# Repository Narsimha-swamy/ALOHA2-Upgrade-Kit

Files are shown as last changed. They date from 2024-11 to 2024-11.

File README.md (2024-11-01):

# Overview 
This is repository is dedicated to upgrading Trossen Robotics ALOHA v1 to ALOHA v2. Bimanual manipulation is an important part of robotics for development of humanoid robots. An enhanced Low cost Open-source HArdware (ALOHA) offers hardware capable of performing bimanual manipulation tasks with a precision of 5-8mm with the ability to collect data via real-time teleoperation. Because of its affordable price many labs  all over the world have bought it from Trossen robotics. But soon after that the team developing ALOHA has released ALOHA v2 to mitigate couple problems that now ALOHA v1 had. The upgrades include new cameras, changed frame, gravity compensation supports for the teleoperator side leader robots and redesigned grippers for low-friction to reduce latency. In this repository you can find different ways you can upgrade the ALOHA v1, the material bill for each of the parts and a zip file that  includes . 

# Details 
The upgrade for ALOHA v2 can be done in 3 stages and these stages are independent of each other and can be done in any order based on the requirement and budget. All the items required for the upgrade are mentioned in the ALOHA 2 upgrade kit excel file the prices are dated as of 10/31/2024. All the cad models required for 3d printing are present in the aloha2 cad models directory.

Stage I - Camera upgrades : This upgrade can be done simply by 3d printing the camera mounts found in the cad models directory and replacing the existing logitech c922x Pro webcams to the new Realsense d405 depth cameras. Optionally if the PC connected to ALOHA doesn't have enough USB ports a 4 port USB Interface PCIe card can installed to the cpu since the cameras need to be connected directly to the motherboard and not the usb hub. This upgrade offers the ability to collect depth, point cloud and voxels data with some processing. 

Stage II - Gripper upgrades : This is the most expensive upgrade in ALOHA 2. This step requires precise 3d prints of both the follower and leader gripper, for its need to be low friction. To build the grippers follow the steps mentioned in the Google's ALOHA 2 Build Instrucitons google doc. And the gripper motors are replaced with the new dynamixel XC430-W150 motors.This upgrade offers better latency during teleoperation. 

Stage III - frame upgrade : This is the most time taking upgrade. This can be done in two approaches 1. Money efficient, 2. Time efficient.  For Money efficient approach we reuse the frame from ALOHA 1, by cutting the frame in required dimensions, by choosing this method you can save $205(USD). In depth tutorial for this will be uploaded soon. For the time efficient upgrade the extrusion bars mentioned in the ALOHA2 upgrade kit can be bought and install it using the procedure mentioned in the Google's ALOHA2 Build Instructions doc. This upgrade offers better frame stability and much better gravity compensation compared to ALOHA v1.

# Notice
All the cad models and the work related to the upgrade belong to the Google'2 ALOHA 2 team. The work in this repository only include a condensed and neat approach to upgrade ALOHA v1 to ALOHA v2 considering both cost and time efficient approaches,  and provide all resources required for the upgrade in one place.

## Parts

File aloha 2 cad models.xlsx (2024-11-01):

Name | Quantity
Mounts
Gravity compensator clip, wrist mount | 2 | Print settings
Gravity compensator clip, elbow mount | 2 | Nylon (pa6)
Camera mount for Viper wrist cam | 2 | Layer height 0.2
Overhead cam mount | 2 | 35-ish% infill, triangular
Worms-eye cam mount | 1 | 4 floor/ceiling layers, 2 wall layers
Widow x gripper
W-bridge_rails_support_v1 1 | 2
W-finger_adaptor_v1 | 4
W-finger_holder_M_v1 | 2
W-gripper_backplate_v1 (acrylic 3mm thickness) | 2
W-hand_holder_v1 | 2
W-rotor_arm_v1 | 4
W-rotor_v1 | 2
W-shim_rotor_v1 | 2
Viper x GRipper
Bridge_rails_support_v1 | 2
Finger_adaptor_v1 | 4
Finger_v1 | 2
Gripper_backplate_v1(acrylic 3mm thickness) | 2
Rotor_arm_v1 | 4
Rotor_v1 | 2
Shim_rotor_v1 | 2
Total 3d prints | 18

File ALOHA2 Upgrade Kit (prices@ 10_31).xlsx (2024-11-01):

Items | Distributor | Qty per package | Qty for one cell | Required packages | Link | Package Price | Price
Frame and Gravity Compensation
8PCS/Set Surface Anodic Oxidation Black L Shape Corner Bracket Plate 5-Hole Outside Joining Plate for 2020 Series Aluminum Profile 3D Printer Frame (Black L-8) | Amazon | 8 | 12 | 2 | https://www.amazon.com/dp/B07ZLSPRXP/ref=twister_B07SZDZG4K?_encoding=UTF8&th=1 | $15.99 | $31.98
316 Stainless Steel Button Head Hex Drive Screws, M5 x 0.8mm Thread, 8mm Long | McMaster | 50 | 70 | 2 | https://www.mcmaster.com/94500A230/ | $8.72 | $17.44
M5 x 12 button head screw, qty 50 | McMaster | 50 | 16 | 1 | https://www.mcmaster.com/92095A210/ | $10.01 | $10.01 | Frame and gravity compensation
M5 x 8 button head screw, qty 100 | McMaster | 100 | 64 | 1 | https://www.mcmaster.com/92095A207/ | $16.33 | $16.33 | $506.16
M5 Post-Assembly Insertion Spring Nuts for 5 Series Aluminum Extrusions | Misumi | 100 | 120 | 2 | https://us.misumi-ec.com/vona2/detail/110302247640/?ProductCode=PACK-SHNTP5-5 | $57.07 | $114.14
Flat-Surface Bracket, 1-7/8" Square | McMaster | 1 | 7 | 7 | https://www.mcmaster.com/1030A15/ | $1.55 | $10.85
Automatic-Return Hanging Retractor without Cable Lock, 1 to 2 lb. Capacity | McMaster | 1 | 2 | 2 | https://www.mcmaster.com/6495A61/ | $55.48 | $110.96
Pulley for Wire Rope-for Horizontal Pull, Single-Groove with Bearing, Swivel Eye, for 3/16" Diameter Rope | McMaster | 1 | 6 | 6 | https://www.mcmaster.com/3213T57/ | $17.24 | $103.44
Music Wire Steel Extension Spring with Loop Ends, 5" Long, 0.5" OD, 0.037" Wire Diameter | McMaster | 3 | 2 | 1 | https://www.mcmaster.com/5108N531/ | $11.52 | $11.52
Rope Guide for 5/8" Maximum Rope Diameter, 316 Stainless Steel | McMaster | 1 | 6 | 6 | https://www.mcmaster.com/8860T129/ | $5.66 | $33.96
8 Pack: 4mm Black Cotton Macramé Cord by Bead Landing | Michaels | 1200 | 3 | 1 | https://www.michaels.com/product/8-pack-darice-craft-designer-cotton-macrame-cord-MP392109 | $45.53 | $45.53
Cameras and Wires
Realsense d405 | Digikey | 1 | 4 | 4 | https://www.digikey.com/en/products/detail/intel-realsense/82635DSD405MP/16265565?s=N4IgTCBcDaIE4FMCGAbAzggdhgBAEwBYAGAVhAF0BfIA | $278.75 | $1115.00 | Camera and wires
USB 3.0 Interface Card PCIe, Fresco FL1100, 4HC, x4, 4Ports | Basler | 1 | 1 | 1 | https://www.baslerweb.com/en-us/shop/usb-3-0-interface-card-pcie-fresco-fl1100-4hc-x4-4ports/ | $195.00 | $195.00 | $1510.49
Female Molex to Male SATA power adapter | Amazon | 3 | 1 | 1 | https://www.amazon.com/Power-Cable-Adapter-Female-8-inch/dp/B07BQFKTG7?s=industrial | $8.99 | $8.99
Sabrent 4-Port USB Hub, USB 3.0 Fast Data Hub with Individual LED Power Switches, 2 Ft Cable, Slim & Portable, for Mac & PC (HB-UM43) | Amazon | 1 | 1 | 1 | https://www.amazon.com/Sabrent-4-Port-Individual-Switches-HB-UM43/dp/B00JX1ZS5O?cv_ct_cx=usb+hub&sbo=RZvfv%2F%2FHxDF%2BO5021pAnSA%3D%3D | $14.50 | $14.50
USB 3.0 A Male to Micro B Male Up Angle with optional Screw Locking Cable, 3m | NTC | 1 | 1 | 1 | https://www.ntcdistributing.com/usb-3-0/a-to-micro-b/a-to-angled-b-cables/usb-3-0-a-male-to-micro-b-male-up-angle-with-optional-screw-locking-cable/ | $42.00 | $42.00
USB 3.0 A Male to Micro B Male Up Angle with optional Screw Locking Cable, 5m | NTC | 1 | 1 | 1 | https://www.ntcdistributing.com/usb-3-0/a-to-micro-b/a-to-angled-b-cables/usb-3-0-a-male-to-micro-b-male-up-angle-with-optional-screw-locking-cable/ | $47.00 | $47.00
USB 3.0 A Male to Micro B Male with M2 Screw Locking Cable, 3m | NTC | 1 | 1 | 1 | https://www.ntcdistributing.com/usb-3-0/a-to-micro-b/a-to-micro-b-with-screw-locking/usb-3-0-a-male-to-micro-b-male-with-m2-screw-locking-cable/ | $40.00 | $40.00
USB 3.0 A Male to Micro B Male with M2 Screw Locking Cable, 5m | NTC | 1 | 1 | 1 | https://www.ntcdistributing.com/usb-3-0/a-to-micro-b/a-to-micro-b-with-screw-locking/usb-3-0-a-male-to-micro-b-male-with-m2-screw-locking-cable/ | $48.00 | $48.00
Grippers
6725K27_5 mm Wide x 120 mm Long Rail Ball Bearing Carriage | McMaster | 1 | 4 | 4 | 6725K23 (https://www.mcmaster.com/6725K23-6725K27/) | $57.60 | $230.40
6725K27_5 mm Wide x 150 mm Long Rail Ball Bearing Carriage | McMaster | 1 | 4 | 4 | 6725K23 (https://www.mcmaster.com/6725K23-6725K28/) | $72.00 | $288.00 | Grippers upgrade
8438K1_Corrosion-Resistant Ball Bearing Carriage | McMaster | 1 | 16 | 16 | 8438K1 (https://www.mcmaster.com/8438K1/) | $92.04 | $1472.64 | $2365.03
Deep Groove Ball Bearing (3mmx6mmx2.5mm) | Amazon | 20 | 24 | 2 | Amazon (https://www.amazon.com/gp/product/B075CMRGY6/ref=ppx_yo_dt_b_asin_image_o01_s00?ie=UTF8&psc=1) | $13.99 | $27.98
M2 Brass Male-Female / Female-Female | Amazon | 1 | 1 | 1 | Amazon (https://www.amazon.com/gp/product/B07ZSZW8T1/ref=ppx_yo_dt_b_asin_title_o05_s00?ie=UTF8&psc=1) | $12.99 | $12.99
Flat Head Screw M3 x 0.5 mm Thread, 10 mm Long | McMaster | 100 | 16 | 1 | 92125A130 (https://www.mcmaster.com/92125A130/) | $7.31 | $7.31
Flat Head Screw M3 x 0.5 mm Thread, 20 mm Long | McMaster | 100 | 8 | 1 | 92125A136 (https://www.mcmaster.com/92125A136/) | $12.86 | $12.86
Flat Head Screw M2 x 0.4 mm Thread, 10 mm Long | McMaster | 100 | 88 | 1 | 92010A005 (https://www.mcmaster.com/92010A005/) | $5.84 | $5.84
Flat Head Screw M2 x 0.4 mm Thread, 16 mm Long | McMaster | 100 | 16 | 1 | 92010A0 08 (https://www.mcmaster.com/92010A008/) | $6.23 | $6.23
Flat Head Screw M2 x 0.4 mm Thread, 20 mm Long | McMaster | 100 | 24 | 1 | 92095A106 (https://www.mcmaster.com/92095A106/) | $5.62 | $5.62
Socket Head Screw M2 x 0.4 mm Thread, 6 mm Long | McMaster | 100 | 8 | 1 | 91292A831 (https://www.mcmaster.com/91292A831/) | $9.28 | $9.28
Hex Nut M2 x 0.4 mm Thread | McMaster | 100 | 64 | 1 | 91828A111 (https://www.mcmaster.com/91828A111/) | $6.14 | $6.14
Flat Head Screw M2.5 x 0.45 mm Thread, 16 mm Long | McMaster | 100 | 16 | 1 | 93395A185 (https://www.mcmaster.com/93395A185/) | $5.62 | $5.62
Steel Washer for M2 Screw Size, 2.200 mm ID, 4.500 mm OD | McMaster | 100 | 32 | 1 | 98688A110 (https://www.mcmaster.com/98688A110/) | $3.15 | $3.15
Short profile button head m2 x6mm (come with rails) |  | 100 | 32 | 1 |  |  | $0.00
M3 Steel Nylon-Insert Locknut | McMaster | 100 | 8 | 1 | 90576A102 (https://www.mcmaster.com/90576A102/) | $4.65 | $4.65
Socket Head Screw M2.5 x 0.45 mm Thread, 8 mm Long | McMaster | 100 | 16 | 1 | 91292A012 (https://www.mcmaster.com/91292A012/) | $6.54 | $6.54
Dynamixel XC430-W150-T servo motor | Robotis | 1 | 2 | 2 | https://www.robotis.us/dynamixel-xc430-w150-t/ | $119.90 | $239.80
CATTONGUE GRIPS Non-Abrasive Anti Slip Grip Tape – 2” Thick Heavy Duty Tape for Indoor & Outdoor, Customizable, Waterproof, & Durable Anti-Slip Tape (Clear, 20ft) | Amazon | 60 | 6 | 1 | https://www.amazon.com/gp/product/B07YB9Q468/ref=ppx_yo_dt_b_search_asin_title?ie=UTF8&th=1 | $19.98 | $19.98
 |  |  |  |  |  |  | Total
 |  |  |  |  |  |  | $4381.68

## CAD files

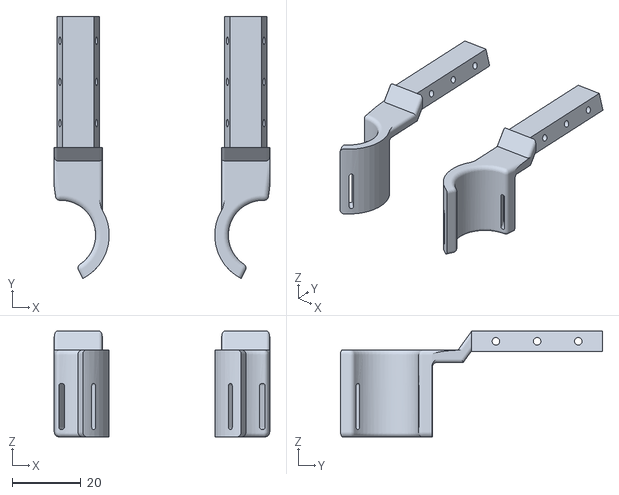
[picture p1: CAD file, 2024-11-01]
aloha2 cad files/W-finger_holder_M_v1.STL
62.8 x 76.3 x 30.9

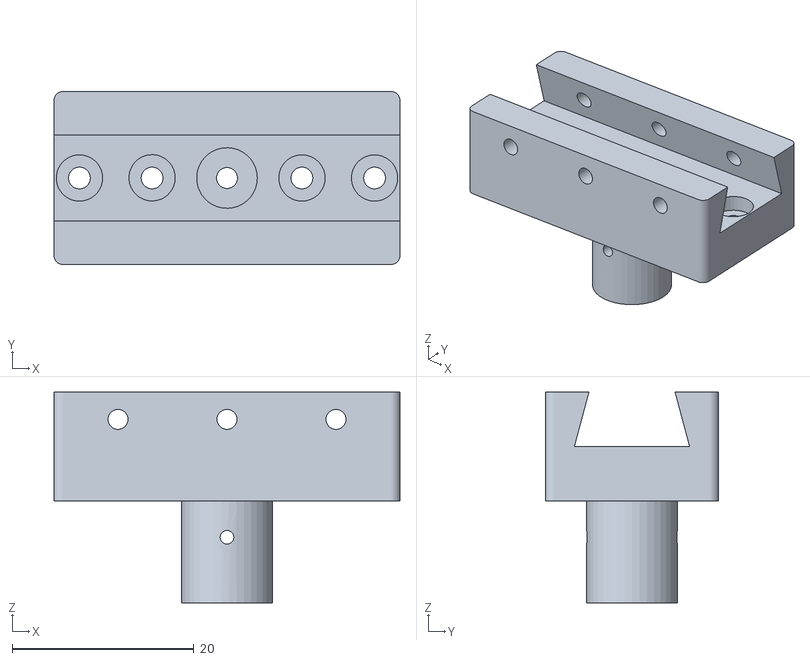
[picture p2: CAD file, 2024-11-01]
aloha2 cad files/W-finger_adaptor_v1.STL
38.1 x 19.1 x 23.2

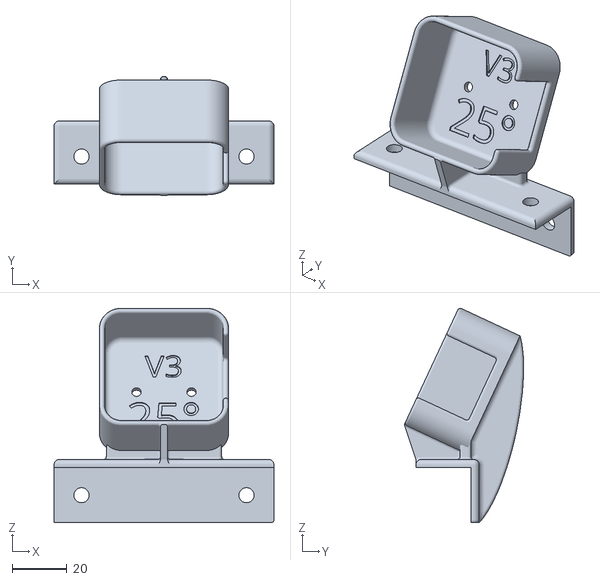
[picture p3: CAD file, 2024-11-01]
aloha2 cad files/RSd405 2020 Overhead Cam Mount v3.stl
80.0 x 43.4 x 78.0

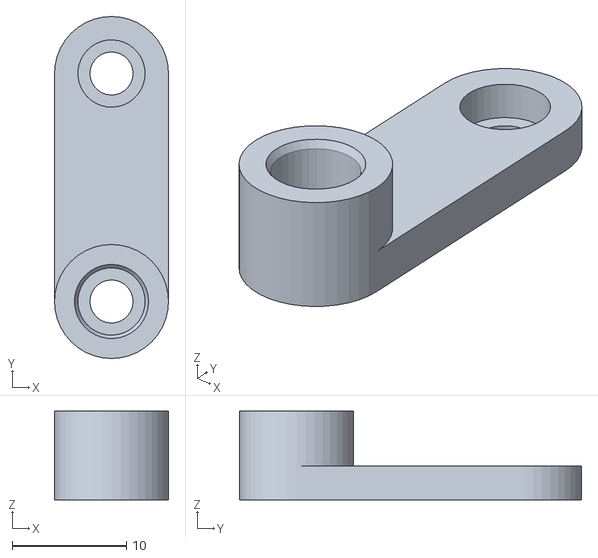
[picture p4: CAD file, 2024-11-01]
aloha2 cad files/W-rotor_arm_v1.STL
10.0 x 30.0 x 7.80

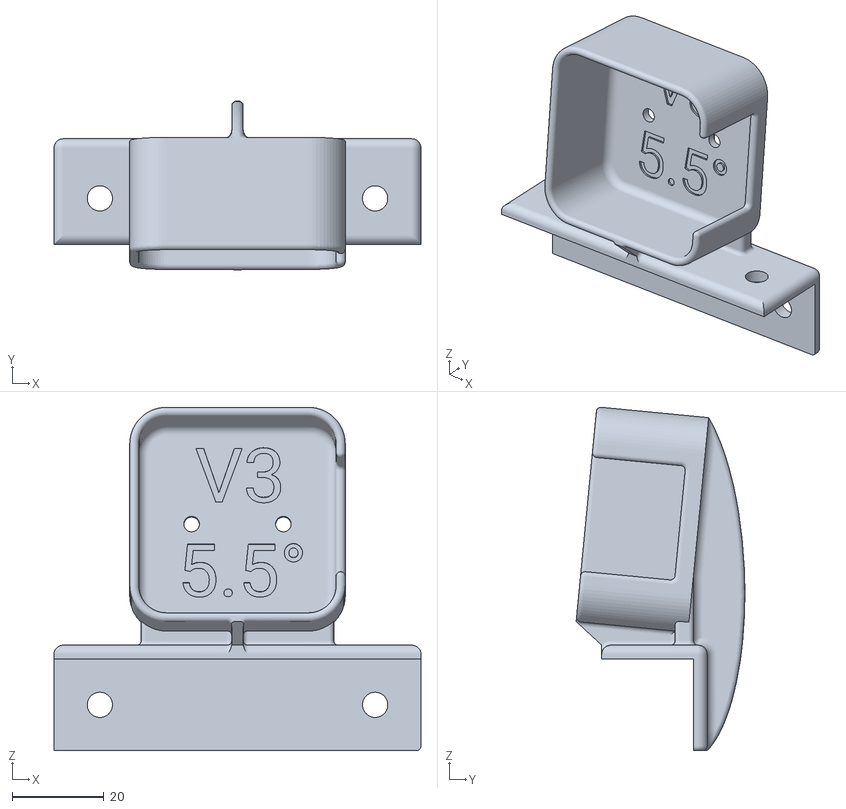
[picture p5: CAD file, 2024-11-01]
aloha2 cad files/RSd405 2020 Worms-eye Cam Mount v3.stl
80.0 x 36.8 x 74.9

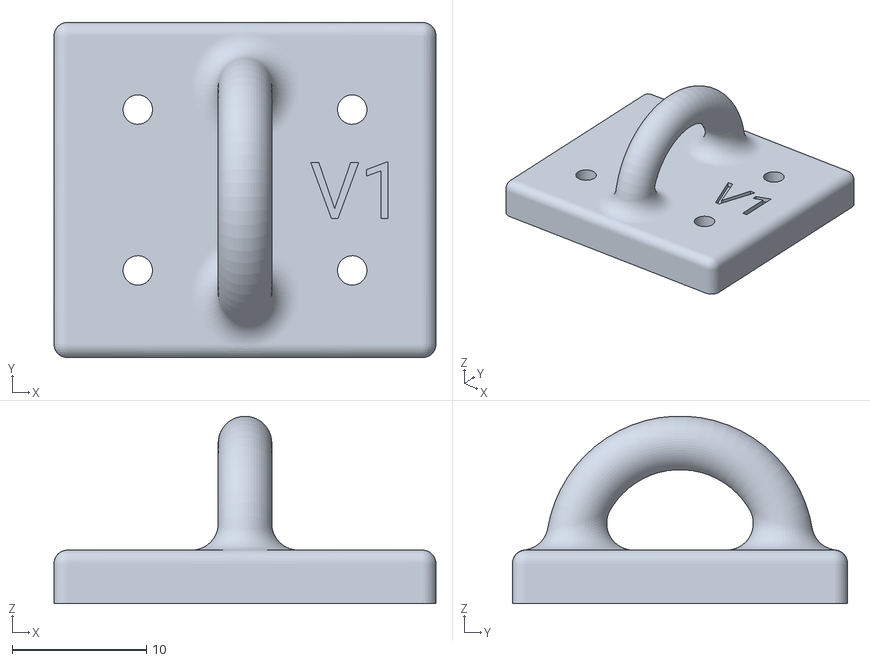
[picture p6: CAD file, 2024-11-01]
aloha2 cad files/Gravity compensator clip, elbow mount.stl
28.5 x 25.0 x 14.0

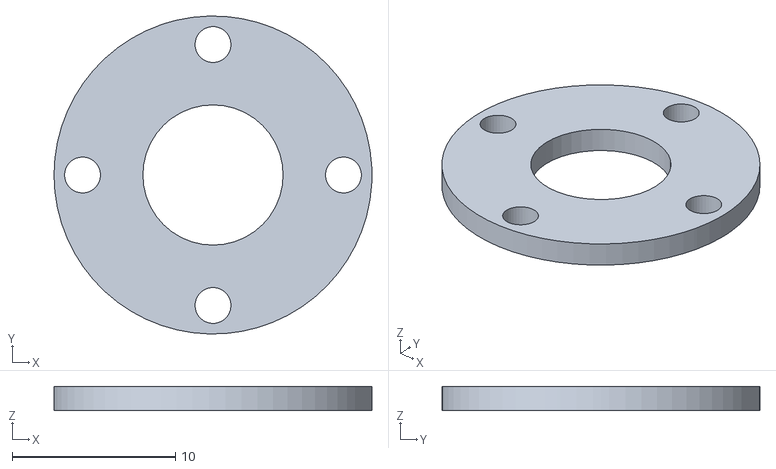
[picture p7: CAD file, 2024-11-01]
aloha2 cad files/Shim_rotor_v1.STL
19.5 x 19.5 x 1.50

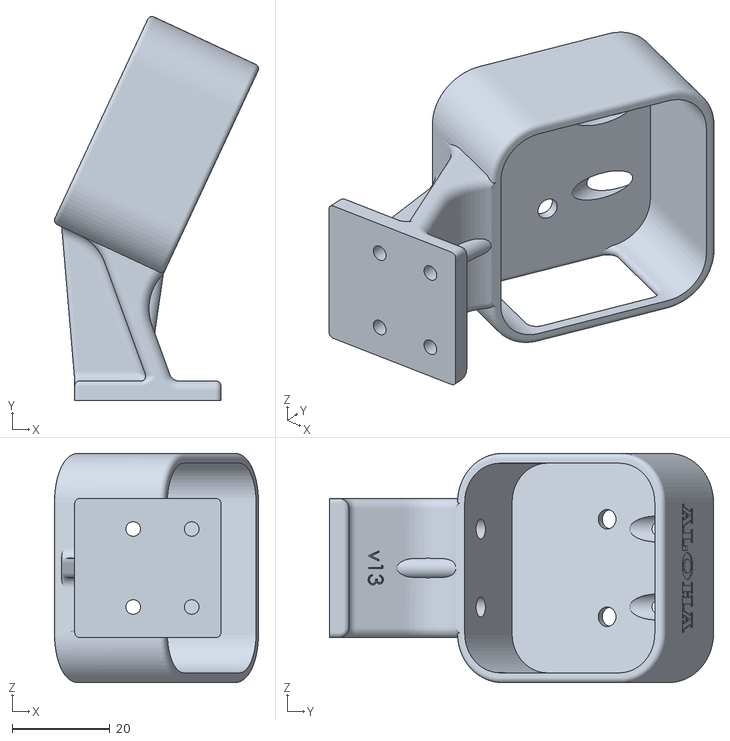
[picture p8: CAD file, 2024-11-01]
aloha2 cad files/Aloha cam wrist mount v13.stl
41.9 x 78.8 x 47.0

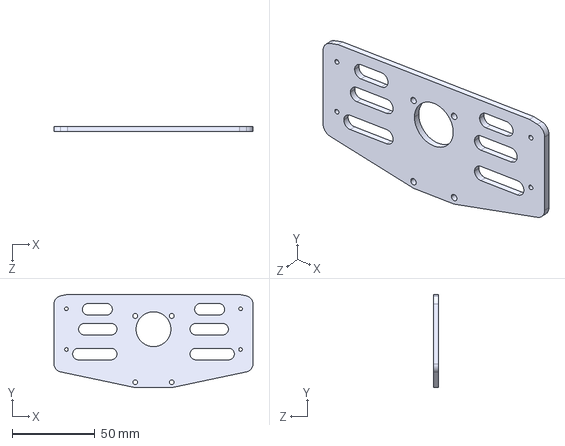
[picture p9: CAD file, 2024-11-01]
aloha2 cad files/W-gripper_backplate_v1.STEP
120.0 x 56.2 x 3.00 mm

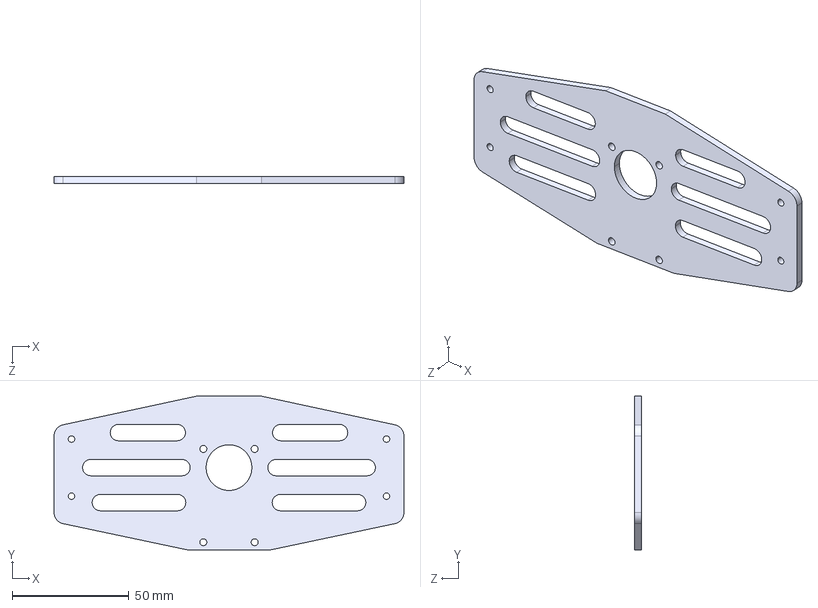
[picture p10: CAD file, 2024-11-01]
aloha2 cad files/Gripper_backplate_v1.STEP
150.0 x 65.9 x 3.00 mm

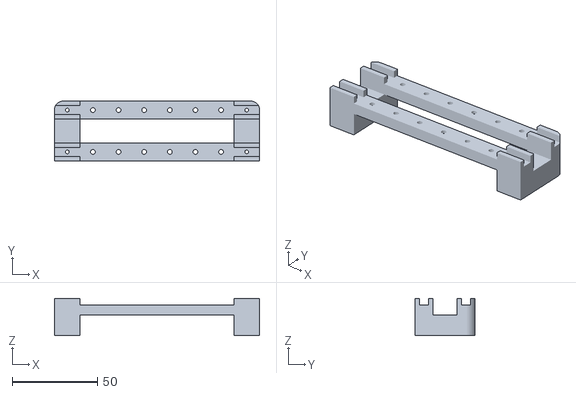
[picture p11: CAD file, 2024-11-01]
aloha2 cad files/W-bridge__rails_support_v1.STL
120.0 x 35.0 x 21.7

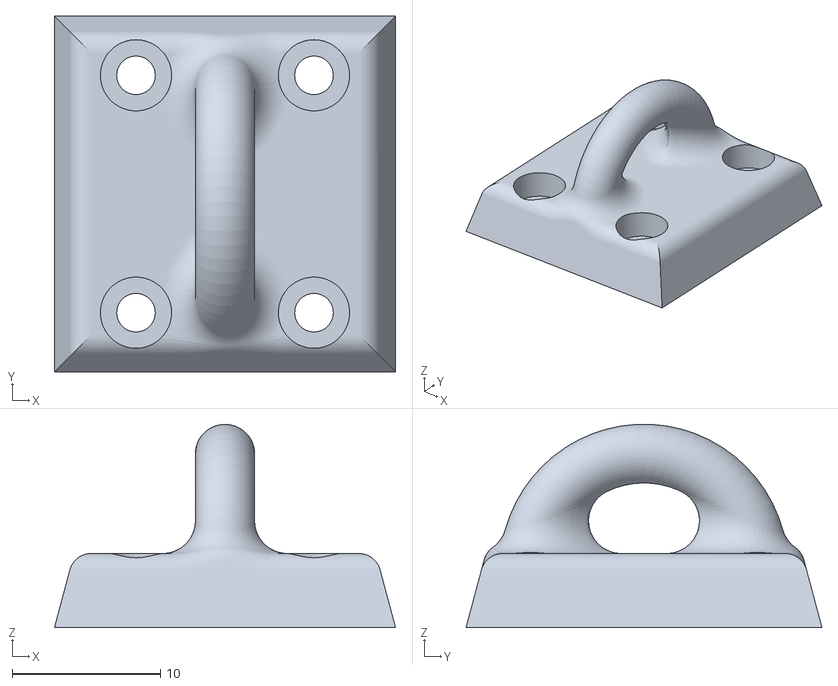
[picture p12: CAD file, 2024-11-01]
aloha2 cad files/Gravity compensator clip, wrist mount.stl
23.0 x 24.0 x 13.7

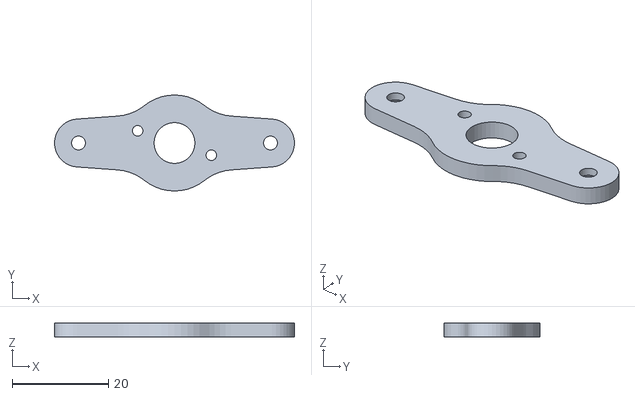
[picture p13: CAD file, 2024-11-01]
aloha2 cad files/W-rotor_v1.STL
50.0 x 20.0 x 3.00

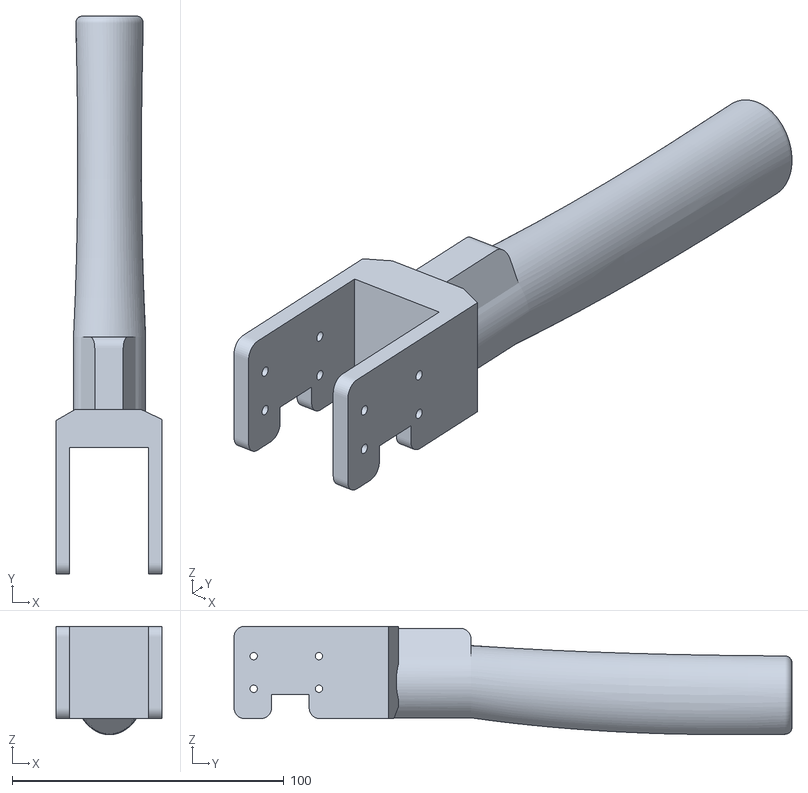
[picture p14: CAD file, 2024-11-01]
aloha2 cad files/W-hand_holder_v1.STL
39.0 x 205.3 x 39.9

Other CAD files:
aloha2 cad files/W-shim_rotor_v1.STL
